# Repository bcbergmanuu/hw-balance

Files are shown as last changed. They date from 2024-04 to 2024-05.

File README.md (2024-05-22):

# Hardware deisgn balanceboard

Design Goals
  - Four measureable legs
  - USB 3 powered (<950mA)
  - Ultralow RMS Noise ldo (0.8µVRMS)
  - 10v Excitation voltage
  - Precision crystal clock fir filtering (20ppm)
  - Class c3 Loadcells type [LA250-D-100kg](https://allscaleseurope.com/content/uploads/2018/01/LA250-D-single-point-load-cell.pdf)
  - 8 bit decoupled auxiliary pc input
  - 24 bit ADC (ad7124)  

Balanceboard design

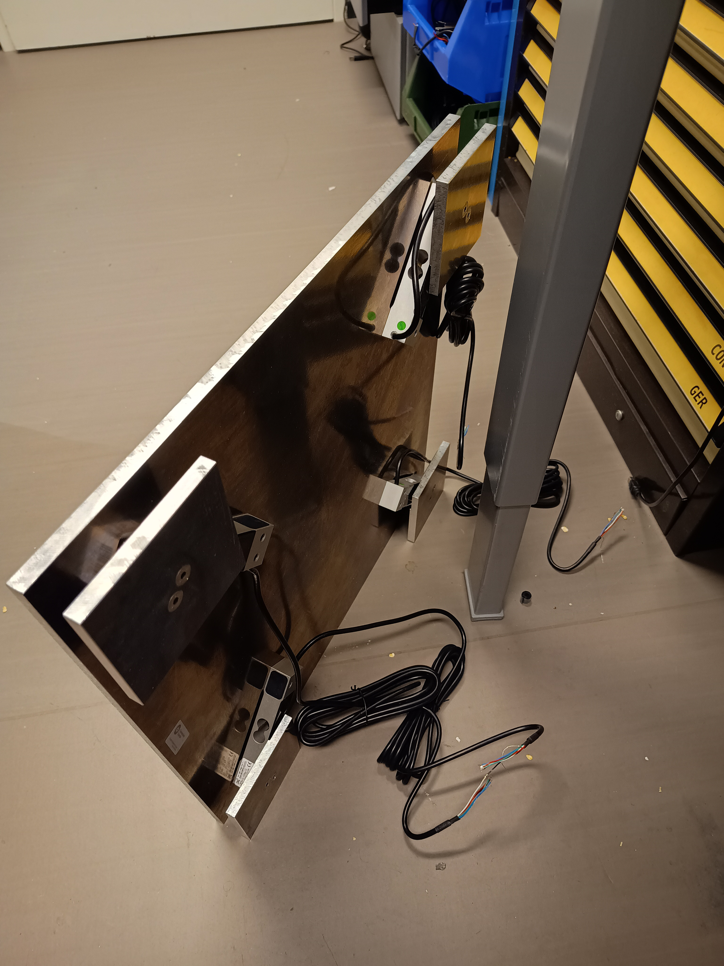
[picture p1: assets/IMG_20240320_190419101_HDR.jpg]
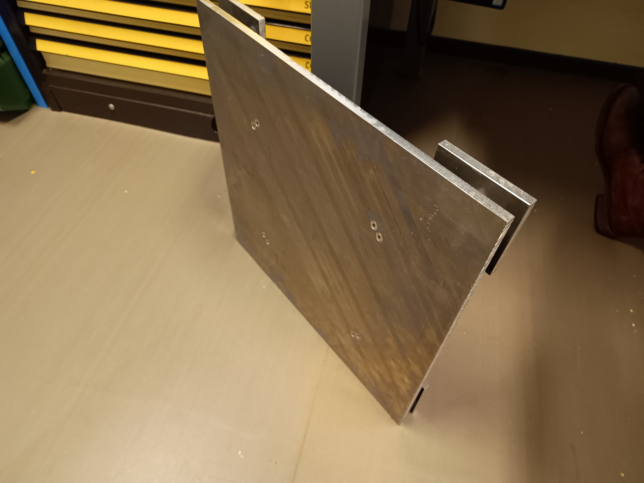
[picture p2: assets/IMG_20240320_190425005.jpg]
 

LTspice simulation LDO | Boost converters

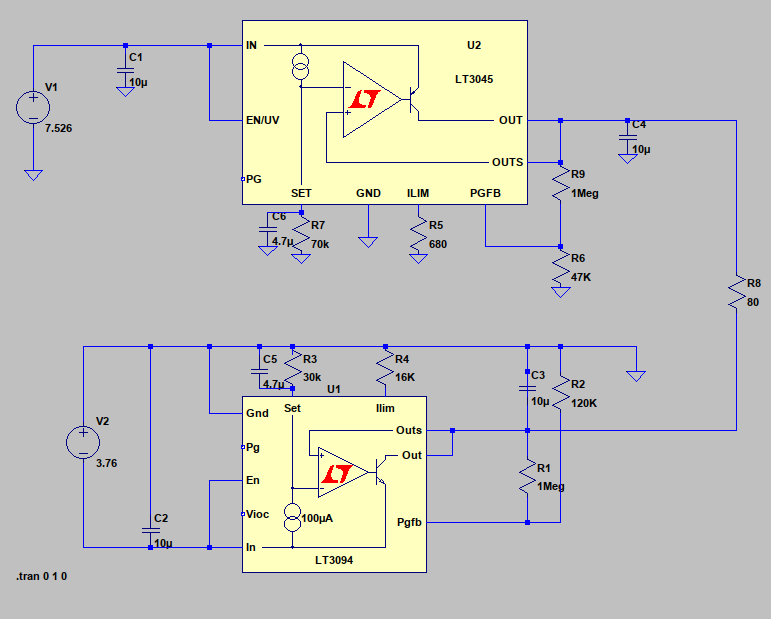
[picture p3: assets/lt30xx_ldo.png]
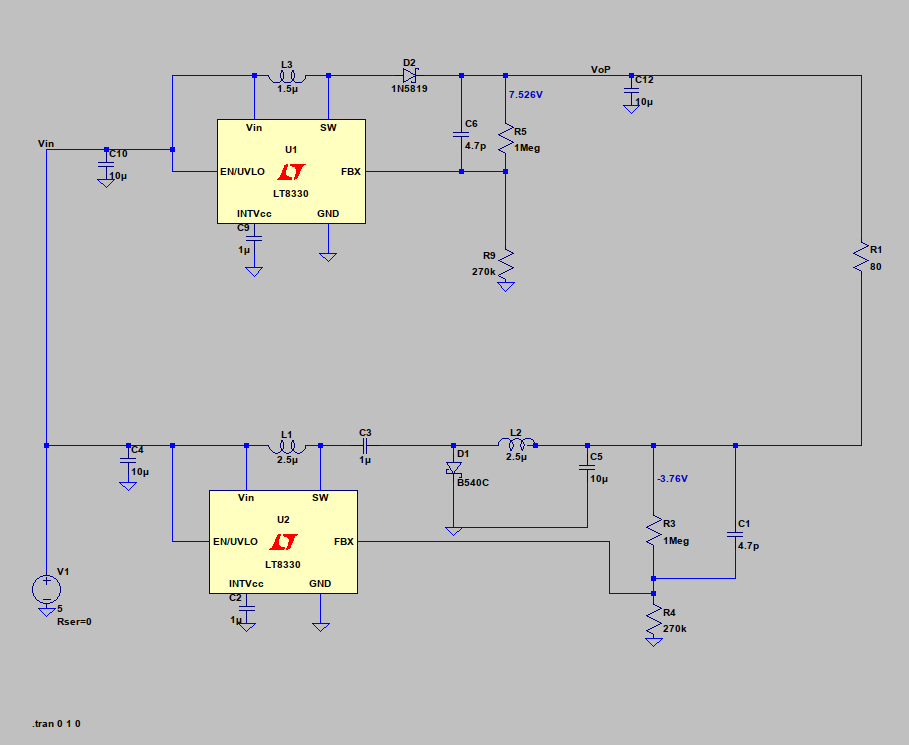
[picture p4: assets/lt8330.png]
 

Schematic Kicad | 3d-view of bcp

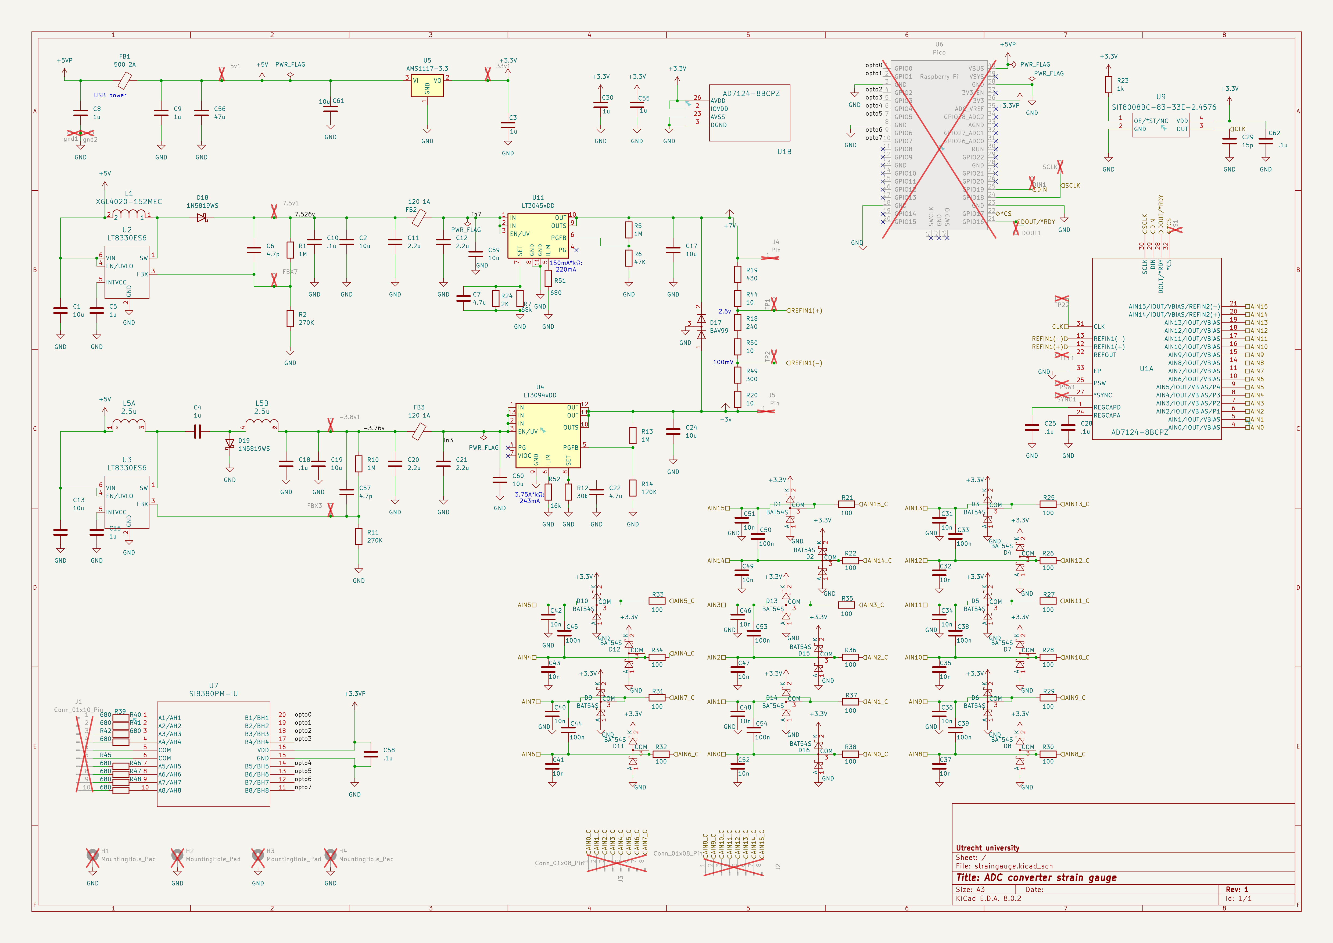
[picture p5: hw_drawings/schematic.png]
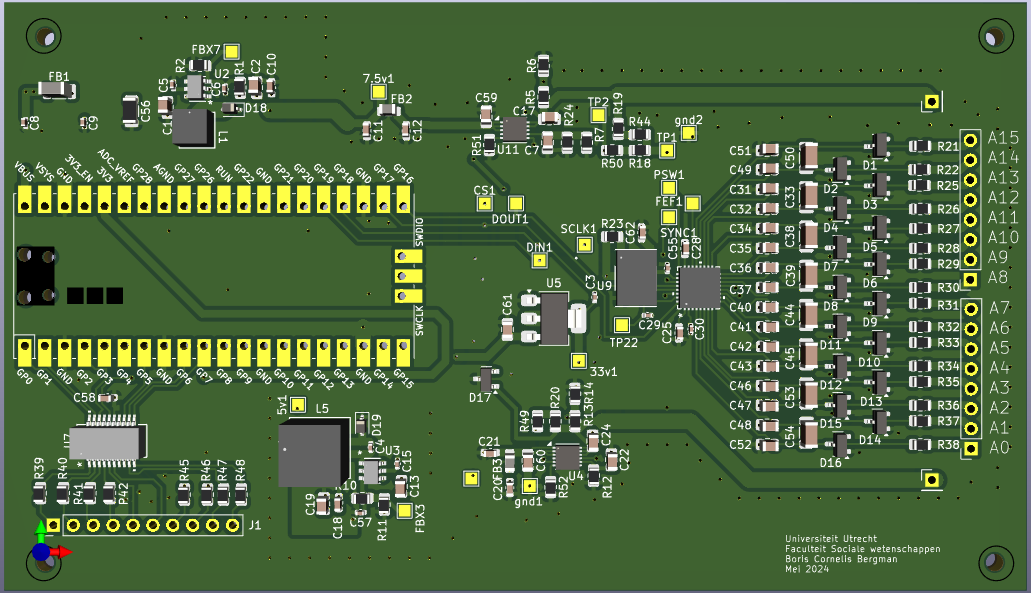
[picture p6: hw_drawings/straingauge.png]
 

Errata:
R19 48K, should be 390
R3 should be removed

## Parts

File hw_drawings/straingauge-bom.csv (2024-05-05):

Id | Designator | Footprint | Quantity | Designation | Supplier and ref
1 | U9 | SIT8008BC-83-33E-10.000000_SIT | 1 | SIT8008BC-83-33E-2.4576
2 | U5,U2 | 05-08-1699_ADI | 2 | LT8333RDD-PBF
3 | U1 | CP_32_12_ADI | 1 | AD7124-8BCPZ
4 | C23,C9,C5,C55,C8,C30,C15 | C_0402_1005Metric | 7 | 1u
5 | FBX7,FBX3,gnd2,7.5v1,PSW1,gnd1,TP2,TP22,DIN1,DOUT1,FEF1,-3.8v1,TP1,5v1,33v1,SYNC1,CS1,SCLK1 | TestPoint_Pad_1.5x1.5mm | 18 | ~
6 | C53,C33,C50,C39,C54,C38,C44,C45 | C_1206_3216Metric | 8 | 100n
7 | R24 | R_0805_2012Metric | 1 | 2K
8 | R6 | R_0805_2012Metric | 1 | 47K
9 | C20,C11,C12,C21 | C_0603_1608Metric | 4 | 2.2u
10 | R19 | R_0805_2012Metric | 1 | 430
11 | C56 | R_1206_3216Metric | 1 | 47u
12 | C43,C51,C34,C37,C31,C52,C40,C36,C49,C35,C48,C41,C47,C42,C32,C46 | C_0805_2012Metric | 16 | 10n
13 | J1 | PinHeader_1x10_P2.54mm_Vertical | 1 | Conn_01x10_Pin
14 | C57,C6 | C_0402_1005Metric | 2 | 4.7p
15 | CR2,CR3 | DIODE_DFN1608D-2_NEX | 2 | PMEG4020EPK_315
16 | R44,R50,R20 | R_0805_2012Metric | 3 | 10
17 | R3,R7 | R_0805_2012Metric | 2 | 68k
18 | R34,R28,R38,R25,R31,R32,R33,R36,R22,R27,R29,R37,R30,R21,R35,R26 | R_0805_2012Metric | 16 | 100
19 | D8,D16,D7,D2,D14,D9,D1,D4,D15,D3,D10,D6,D13,D11,D12,D5 | SOT-23 | 16 | BAT54S
20 | U4 | DFN-12-1EP_3x3mm_P0.45mm_EP1.65x2.38mm_ThermalVias | 1 | LT3094xDD
21 | R14 | R_0805_2012Metric | 1 | 120K
22 | R41,R45,R42,R48,R47,R39,R40,R46 | R_0805_2012Metric | 8 | 680
23 | R5,R16,R1,R10,R13 | R_0805_2012Metric | 5 | 1M
24 | C4,C25,C62,C14,C58,C10,C18,C28 | C_0603_1608Metric | 8 | .1u
25 | R43 | R_0805_2012Metric | 1 | 10k
26 | C13,C60,C24,C59,C1,C2,C19,C27,C17,C61 | C_0805_2012Metric | 10 | 10u
27 | L5 | IC4_MSD7342-252MLB_COC | 1 | 2.5u
28 | U7 | QSOP20_SIL | 1 | SI8380PM-IU
29 | R2,R11 | R_0805_2012Metric | 2 | 270K
30 | R4,R8 | R_0805_2012Metric | 2 | 20k
31 | C26,C22,C7 | C_0805_2012Metric | 3 | 4.7u
32 | J2,J3 | PinSocket_1x08_P2.54mm_Vertical | 2 | Conn_01x08_Pin
33 | L1 | IND_XGL4020_COC | 1 | XGL4020-152MEC
34 | L3,L4 | IND_NFZ18SM121SN10D_MUR | 2 | NFZ18SM121SN10D
35 | R23 | R_0805_2012Metric | 1 | 1k
36 | U6 | RPi_Pico_SMD_TH | 1 | Pico
37 | R15 | R_0805_2012Metric | 1 | 33k
38 | J4,J5 | PinHeader_1x01_P2.54mm_Vertical | 2 | Pin
39 | R18 | R_0805_2012Metric | 1 | 240
40 | R49 | R_0805_2012Metric | 1 | 300
41 | R17 | R_0805_2012Metric | 1 | 100k
42 | R9 | R_0805_2012Metric | 1 | 39k
43 | C29 | C_0402_1005Metric | 1 | 15p
44 | C3 | C_0603_1608Metric | 1 | 680p
45 | L2 | IND_742792040_WRE | 1 | 742792040
46 | U11,U10 | DFN-10-1EP_3x3mm_P0.5mm_EP1.65x2.38mm | 2 | LT3045xDD
47 | R12 | R_0805_2012Metric | 1 | 30k
48 | C16 | C_0603_1608Metric | 1 | 1.5n

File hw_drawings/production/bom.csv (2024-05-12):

Designator | Footprint | Quantity | Value | LCSC Part #
C1, C13, C17, C19, C2, C24, C59, C60, C61 | 0805 | 9 | 10u | C15850
C10, C18, C25, C28, C58, C62 | 0603 | 6 | .1u | C14663
C11, C12, C20, C21 | 0603 | 4 | 2.2u | C377773
C15, C3, C30, C4, C5, C55, C8, C9 | 0402 | 8 | 1u | C52923
C22, C7 | 0805 | 2 | 4.7u | C1779
C29 | 0402 | 1 | 15p | C1548
C31, C32, C34, C35, C36, C37, C40, C41, C42, C43, C46, C47, C48, C49, C51, C52 | 0805 | 16 | 10n | C441760
C33, C38, C39, C44, C45, C50, C53, C54 | 1206 | 8 | 100n | C338082
C56 | 1206 | 1 | 47u | C96123
C57, C6 | 0402 | 2 | 4.7p | C1569
D1, D10, D11, D12, D13, D14, D15, D16, D2, D3, D4, D5, D6, D7, D8, D9 | SOT-23 | 16 | BAT54S | C727126
D17 | SOT-23 | 1 | BAV99 | C2500
D18, D19 | D_SOD-323 | 2 | 1N5819WS | C191023
FB1 | 1206 | 1 | 500 2A | C515371
FB2, FB3 | 0805 | 2 | 120 1A | C2844587
L1 | IND_XGL4020_COC | 1 | XGL4020-152MEC
L5 | IC4_MSD7342-252MLB_COC | 1 | 2.5u
R1, R10, R13, R5 | 0805 | 4 | 1M | C17514
R11, R2 | 0805 | 2 | 270K | C17589
R12 | 0805 | 1 | 30k | C17621
R14 | 0805 | 1 | 120K | C17436
R18 | 0805 | 1 | 240 | C17572
R19 | 0805 | 1 | 430 | C17695
R20, R44, R50 | 0805 | 3 | 10 | C17415
R21, R22, R25, R26, R27, R28, R29, R30, R31, R32, R33, R34, R35, R36, R37, R38 | 0805 | 16 | 100 | C17408
R23 | 0805 | 1 | 1k | C17513
R24 | 0805 | 1 | 2K | C17604
R39, R40, R41, R42, R45, R46, R47, R48 | 0805 | 8 | 680 | C17798
R49 | 0805 | 1 | 300 | C17630
R51 | 0805 | 1 | 680
R52 | 0805 | 1 | 16k | C17490
R6 | 0805 | 1 | 47K | C17713
R7 | 0805 | 1 | 68k | C17801
U1 | CP_32_12_ADI | 1 | AD7124-8BCPZ | C97314
U11 | DFN-10-1EP_3x3mm_P0.5mm_EP1.65x2.38mm | 1 | LT3045xDD | C666574
U2, U3 | TSOT-23_S6_LIT | 2 | LT8330ES6 | C673741
U4 | DFN-12-1EP_3x3mm_P0.45mm_EP1.65x2.38mm_ThermalVias | 1 | LT3094xDD | C670492
U5 | SOT-223-3_TabPin2 | 1 | AMS1117-3.3 | C6186
U7 | QSOP20_SIL | 1 | SI8380PM-IU | C7315580
U9 | SIT8008BC-83-33E-10.000000_SIT | 1 | SIT8008BC-83-33E-2.4576

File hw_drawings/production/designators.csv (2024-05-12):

-3.8v1:1
33v1:1
5v1:1
7.5v1:1
C1:1
C10:1
C11:1
C12:1
C13:1
C15:1
C17:1
C18:1
C19:1
C2:1
C20:1
C21:1
C22:1
C24:1
C25:1
C28:1
C29:1
C3:1
C30:1
C31:1
C32:1
C33:1
C34:1
C35:1
C36:1
C37:1
C38:1
C39:1
C4:1
C40:1
C41:1
C42:1
C43:1
C44:1
C45:1
C46:1
C47:1
C48:1
C49:1
C5:1
C50:1
C51:1
C52:1
C53:1
C54:1
C55:1
C56:1
C57:1
C58:1
C59:1
C6:1
C60:1
C61:1
C62:1
C7:1
C8:1
C9:1
CS1:1
D1:1
D10:1
D11:1
D12:1
D13:1
D14:1
D15:1
D16:1
D17:1
D18:1
D19:1
D2:1
D3:1
D4:1
D5:1
D6:1
D7:1
D8:1
D9:1
DIN1:1
DOUT1:1
FB1:1
FB2:1
FB3:1
FBX3:1
FBX7:1
FEF1:1
H1:1
H2:1
H3:1
H4:1
J1:1
J2:1
J3:1
J4:1
J5:1
L1:1
L5:1
PSW1:1
R1:1
R10:1
R11:1
R12:1
R13:1
R14:1
R18:1
R19:1
R2:1
R20:1
R21:1
R22:1
R23:1
R24:1
R25:1
R26:1
R27:1
R28:1
R29:1
R30:1
R31:1
R32:1
R33:1
R34:1
R35:1
R36:1
R37:1
R38:1
R39:1
R40:1
R41:1
R42:1
R44:1
R45:1
R46:1
R47:1
R48:1
R49:1
R5:1
R50:1
R51:1
R52:1
R6:1
R7:1
SCLK1:1
SYNC1:1
TP1:1
TP2:1
TP22:1
U1:1
U11:1
U2:1
U3:1
U4:1
U5:1
U6:1
U7:1
U9:1
gnd1:1
gnd2:1

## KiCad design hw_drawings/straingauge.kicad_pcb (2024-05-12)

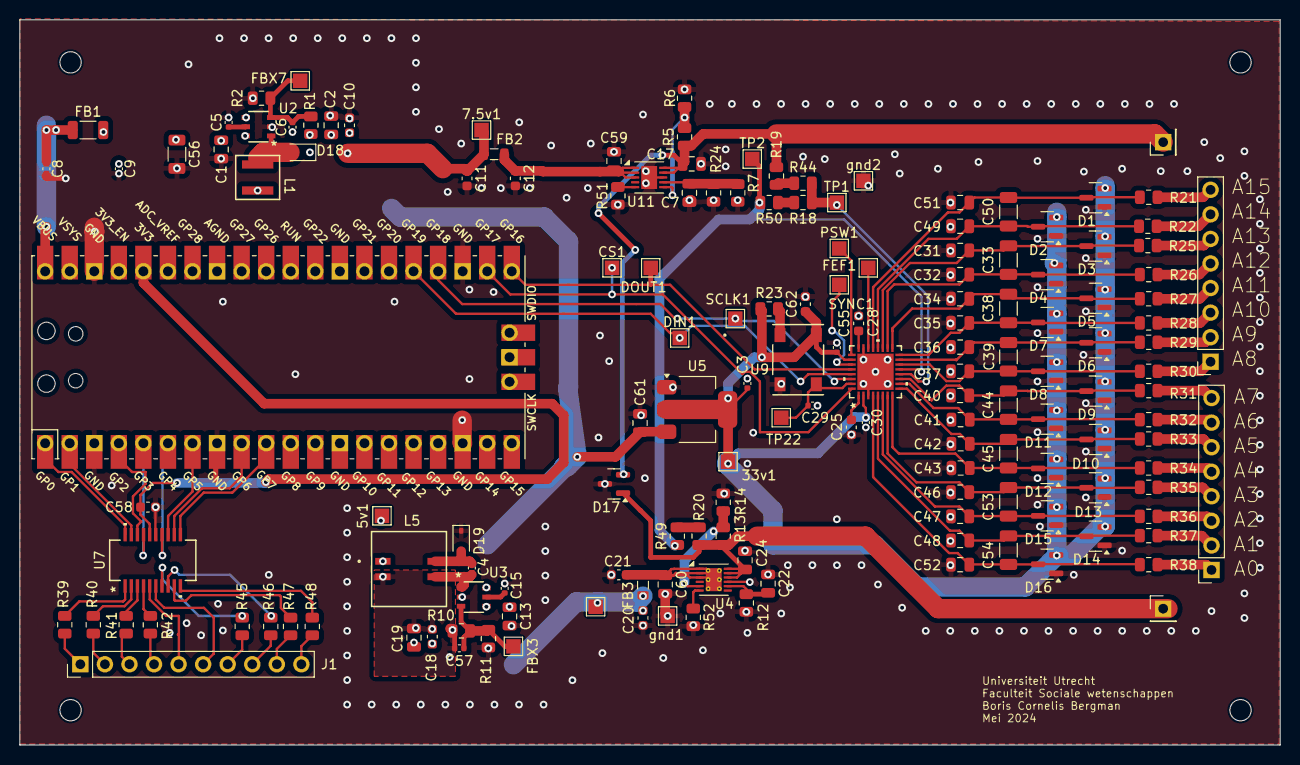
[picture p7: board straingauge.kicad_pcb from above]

Board: 4 copper layers, 130.3 x 75.0 mm, 161 parts (0 on the bottom side), 98 nets.

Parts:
5v1, 7.5v1, 33v1: TestPoint_Pad_1.5x1.5mm
-3.8v1: TestPoint_Pad_1.5x1.5mm
C1, C2, C13, C17, C19, C24, C59, C60, C61: 10u; C_0805_2012Metric
C3, C4, C5, C8, C9, C15, C30, C55: 1u; C_0402_1005Metric
C6, C57: 4.7p; C_0402_1005Metric
C7, C22: 4.7u; C_0805_2012Metric
C10, C18, C25, C28, C58, C62: .1u; C_0603_1608Metric
C11, C12, C20, C21: 2.2u; C_0603_1608Metric
C29: 15p; C_0402_1005Metric
C31, C32, C34, C35, C36, C37, C40, C41, C42, C43, C46, C47, C48, C49, C51, C52: 10n; C_0805_2012Metric
C33, C38, C39, C44, C45, C50, C53, C54: 100n; C_1206_3216Metric
C56: 47u; R_1206_3216Metric
CS1: TestPoint_Pad_1.5x1.5mm
D1, D2, D3, D4, D5, D6, D7, D8, D9, D10, D11, D12, D13, D14, D15, D16: BAT54S; SOT-23
D17: BAV99; SOT-23
D18, D19: 1N5819WS; D_SOD-323
DIN1: TestPoint_Pad_1.5x1.5mm
DOUT1: TestPoint_Pad_1.5x1.5mm
FB1: 500 2A; L_1206_3216Metric
FB2, FB3: 120 1A; L_0805_2012Metric
FBX3, FBX7: TestPoint_Pad_1.5x1.5mm
FEF1: TestPoint_Pad_1.5x1.5mm
H1, H2, H3, H4: MountingHole_Pad; MountingHole_2.2mm_M2
J1: Conn_01x10_Pin; PinHeader_1x10_P2.54mm_Vertical
J2, J3: Conn_01x08_Pin; PinSocket_1x08_P2.54mm_Vertical
J4, J5: Pin; PinHeader_1x01_P2.54mm_Vertical
L1: XGL4020-152MEC; IND_XGL4020_COC
L5: 2.5u; IC4_MSD7342-252MLB_COC
PSW1: TestPoint_Pad_1.5x1.5mm
R1, R5, R10, R13: 1M; R_0805_2012Metric
R2, R11: 270K; R_0805_2012Metric
R6: 47K; R_0805_2012Metric
R7: 68k; R_0805_2012Metric
R12: 30k; R_0805_2012Metric
R14: 120K; R_0805_2012Metric
R18: 240; R_0805_2012Metric
R19: 430; R_0805_2012Metric
R20, R44, R50: 10; R_0805_2012Metric
R21, R22, R25, R26, R27, R28, R29, R30, R31, R32, R33, R34, R35, R36, R37, R38: 100; R_0805_2012Metric
R23: 1k; R_0805_2012Metric
R24: 2K; R_0805_2012Metric
R39, R40, R41, R42, R45, R46, R47, R48, R51: 680; R_0805_2012Metric
R49: 300; R_0805_2012Metric
R52: 16k; R_0805_2012Metric
SCLK1: TestPoint_Pad_1.5x1.5mm
SYNC1: TestPoint_Pad_1.5x1.5mm
TP1, TP2, TP22: TestPoint_Pad_1.5x1.5mm
U1: AD7124-8BCPZ; CP_32_12_ADI
U2, U3: LT8330ES6; TSOT-23_S6_LIT
U4: LT3094xDD; DFN-12-1EP_3x3mm_P0.45mm_EP1.65x2.38mm_ThermalVias
U5: AMS1117-3.3; SOT-223-3_TabPin2
U6: Pico; RPi_Pico_SMD_TH
U7: SI8380PM-IU; QSOP20_SIL
U9: SIT8008BC-83-33E-2.4576; SIT8008BC-83-33E-10.000000_SIT
U11: LT3045xDD; DFN-10-1EP_3x3mm_P0.5mm_EP1.65x2.38mm
gnd1, gnd2: TestPoint_Pad_1.5x1.5mm

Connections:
+3.3V: 33v1.1, C3.1, C30.1, C55.1, C62.1, D1.2 (K), D2.2 (K), D3.2 (K), D4.2 (K), D5.2 (K), D6.2 (K), D7.2 (K), D8.2 (K), D9.2 (K), D10.2 (K), D11.2 (K), D12.2 (K), D13.2 (K), D14.2 (K), D15.2 (K), D16.2 (K), R23.1, U1.2 (IOVDD), U1.26 (AVDD), U5.2 (VO), U9.4 (VDD)
+3.3VP: C58.1, U6.36 (3V3), U7.16 (VDD)
+5V: 5v1.1, C1.1, C9.1, C13.1, C56.1, C61.1, FB1.2, L1.2, L5.1, U2.4 (EN/UVLO), U2.6 (VIN), U3.4 (EN/UVLO), U3.6 (VIN), U5.3 (VI)
+5VP: C8.1, FB1.1, U6.40 (VBUS)
+7V: C17.1, D17.2 (A), J4.1, R5.1, R19.1, U11.9 (OUTS), U11.10 (OUT)
-3v: C24.1, D17.1 (K), J5.1, R13.2, R20.2, U4.10 (OUTS), U4.11 (OUT), U4.12 (OUT)
/7.526v: 7.5v1.1, C2.1, C6.1, C10.1, C11.1, D18.1 (K), FB2.1, R1.1
/*CS: CS1.1, U1.32 (*CS), U6.22 (GPIO17)
/-3.76v: -3.8v1.1, C18.2, C19.1, C20.1, C57.1, FB3.1, L5.2, R10.2
/AIN0: C52.2, C54.1, D16.3 (COM), R38.1, U1.4 (AIN0/IOUT/VBIAS)
/AIN0_C: J3.1, R38.2
/AIN1: C48.1, C54.2, D14.3 (COM), R37.1, U1.5 (AIN1/IOUT/VBIAS)
/AIN1_C: J3.2, R37.2
/AIN2: C47.2, C53.1, D15.3 (COM), R36.1, U1.6 (AIN2/IOUT/VBIAS/P1)
/AIN2_C: J3.3, R36.2
/AIN3: C46.1, C53.2, D13.3 (COM), R35.1, U1.7 (AIN3/IOUT/VBIAS/P2)
/AIN3_C: J3.4, R35.2
/AIN4: C43.2, C45.1, D12.3 (COM), R34.1, U1.8 (AIN4/IOUT/VBIAS/P3)
/AIN4_C: J3.5, R34.2
/AIN5: C42.1, C45.2, D10.3 (COM), R33.1, U1.9 (AIN5/IOUT/VBIAS/P4)
/AIN5_C: J3.6, R33.2
/AIN6: C41.2, C44.1, D11.3 (COM), R32.1, U1.10 (AIN6/IOUT/VBIAS)
/AIN6_C: J3.7, R32.2
/AIN7: C40.1, C44.2, D9.3 (COM), R31.1, U1.11 (AIN7/IOUT/VBIAS)
/AIN7_C: J3.8, R31.2
/AIN8: C37.2, C39.1, D8.3 (COM), R30.1, U1.14 (AIN8/IOUT/VBIAS)
/AIN8_C: J2.1, R30.2
/AIN9: C36.1, C39.2, D6.3 (COM), R29.1, U1.15 (AIN9/IOUT/VBIAS)
/AIN9_C: J2.2, R29.2
/AIN10: C35.2, C38.1, D7.3 (COM), R28.1, U1.16 (AIN10/IOUT/VBIAS)
/AIN10_C: J2.3, R28.2
/AIN11: C34.1, C38.2, D5.3 (COM), R27.1, U1.17 (AIN11/IOUT/VBIAS)
/AIN11_C: J2.4, R27.2
/AIN12: C32.2, C33.1, D4.3 (COM), R26.1, U1.18 (AIN12/IOUT/VBIAS)
/AIN12_C: J2.5, R26.2
/AIN13: C31.1, C33.2, D3.3 (COM), R25.1, U1.19 (AIN13/IOUT/VBIAS)
/AIN13_C: J2.6, R25.2
/AIN14: C49.2, C50.1, D2.3 (COM), R22.1, U1.20 (AIN14/IOUT/VBIAS/REFIN2(+))
/AIN14_C: J2.7, R22.2
/AIN15: C50.2, C51.1, D1.3 (COM), R21.1, U1.21 (AIN15/IOUT/VBIAS/REFIN2(-))
/AIN15_C: J2.8, R21.2
/CLK: C29.1, TP22.1, U1.31 (CLK), U9.3 (OUT)
/DIN: DIN1.1, U1.29 (DIN), U6.25 (GPIO19)
/DOUT/*RDY: DOUT1.1, U1.28 (DOUT/*RDY), U6.21 (GPIO16)
/REFIN1(+): R18.1, R44.2, TP1.1, U1.12 (REFIN1(+))
/REFIN1(-): R49.1, R50.2, TP2.1, U1.13 (REFIN1(-))
/SCLK: SCLK1.1, U1.30 (SCLK), U6.24 (GPIO18)
/in3: C21.1, C60.1, FB3.2, U4.1 (IN), U4.2 (IN), U4.3 (EN/UV), U4.13 (IN)
/in7: C12.1, C59.1, FB2.2, U11.1 (IN), U11.2 (IN), U11.3 (EN/UV)
/opto0: U6.1 (GPIO0), U7.20 (B1/BH1)
/opto1: U6.2 (GPIO1), U7.19 (B2/BH2)
/opto2: U6.4 (GPIO2), U7.18 (B3/BH3)
/opto3: U6.5 (GPIO3), U7.17 (B4/BH4)
/opto4: U6.6 (GPIO4), U7.14 (B5/BH5)
/opto5: U6.7 (GPIO5), U7.13 (B6/BH6)
/opto6: U6.9 (GPIO6), U7.12 (B7/BH7)
/opto7: U6.10 (GPIO7), U7.11 (B8/BH8)
GND: C1.2, C2.2, C3.2, C5.1, C7.2, C8.2, C9.2, C10.2, C11.2, C12.2, C13.2, C15.1, C17.2, C18.1, C19.2, C20.2, C21.2, C22.1, C24.2, C25.2, C28.2, C29.2, C30.2, C31.2, C32.1, C34.2, C35.1, C36.2, C37.1, C40.2, C41.1, C42.2, C43.1, C46.2, C47.1, C48.2, C49.1, C51.2, C52.1, C55.2, C56.2, C58.2, C59.2, C60.2, C61.2, C62.2, D1.1 (A), D2.1 (A), D3.1 (A), D4.1 (A), D5.1 (A), D6.1 (A), D7.1 (A), D8.1 (A), D9.1 (A), D10.1 (A), D11.1 (A), D12.1 (A), D13.1 (A), D14.1 (A), D15.1 (A), D16.1 (A), D17.3 (K), D19.1 (K), R2.2, R6.2, R7.2, R11.1, R12.1, R14.1, R24.2, R51.2, R52.2, U1.3 (DGND), U1.23 (AVSS), U1.33 (EP), U2.2 (GND), U3.2 (GND), U4.9 (GND), U5.1 (GND), U6.3 (GND), U6.8 (GND), U6.18 (GND), U6.23 (GND), U6.38 (GND), U7.15 (GND), U9.2 (GND), U11.8 (GND), U11.11 (GND), gnd1.1, gnd2.1
unnamed: D18.2 (A), L1.1, U2.1 (SW)
unnamed: C4.2, D19.2 (A), L5.4
unnamed: J1.1, R39.1
unnamed: J1.2, R40.1
unnamed: J1.3, R41.1
unnamed: J1.4, R42.1
unnamed: J1.5, U7.5 (COM)
unnamed: J1.6, U7.6 (COM)
unnamed: J1.7, R45.1
unnamed: J1.8, R46.1
unnamed: J1.9, R47.1
unnamed: J1.10, R48.1
unnamed: R18.2, R50.1
unnamed: R19.2, R44.1
unnamed: R20.1, R49.2
unnamed: SYNC1.1, U1.27 (*SYNC)
unnamed: PSW1.1, U1.25 (PSW)
unnamed: FEF1.1, U1.22 (REFOUT)
unnamed: C28.1, U1.24 (REGCAPA)
unnamed: C25.1, U1.1 (REGCAPD)
unnamed: C6.2, FBX7.1, R1.2, R2.1, U2.3 (FBX)
unnamed: C5.2, U2.5 (INTVCC)
unnamed: C57.2, FBX3.1, R10.1, R11.2, U3.3 (FBX)
unnamed: C15.2, U3.5 (INTVCC)
unnamed: C4.1, L5.3, U3.1 (SW)
unnamed: R52.1, U4.6 (ILIM)
unnamed: R13.1, R14.2, U4.5 (PGFB)
unnamed: C22.2, R12.2, U4.8 (SET)
unnamed: R39.2, U7.1 (A1/AH1)
unnamed: R40.2, U7.2 (A2/AH2)
unnamed: R41.2, U7.3 (A3/AH3)
unnamed: R42.2, U7.4 (A4/AH4)
unnamed: R45.2, U7.7 (A5/AH5)
unnamed: R46.2, U7.8 (A6/AH6)
unnamed: R47.2, U7.9 (A7/AH7)
unnamed: R48.2, U7.10 (A8/AH8)
unnamed: R23.2, U9.1 (OE/*ST/NC)
unnamed: R51.1, U11.5 (ILIM)
unnamed: R5.2, R6.1, U11.6 (PGFB)
unnamed: C7.1, R7.1, R24.1, U11.7 (SET)

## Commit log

2024-04-29 drawing schematic
    [straingauge.kicad_pcb, straingauge.kicad_sch]
2024-04-30 finished schematic
    [straingauge.kicad_pcb, straingauge.kicad_sch]
2024-05-02 fixed ERC
    [straingauge.kicad_pcb, straingauge.kicad_sch]
2024-05-03 full pcb
    [straingauge.kicad_pcb, straingauge.kicad_sch]
2024-05-03 full pcb1
    [straingauge.kicad_pcb, straingauge.kicad_sch]
2024-05-05 finished project
    [straingauge-bom.csv, straingauge-job.gbrjob, straingauge.csv, straingauge.kicad_pcb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]
2024-05-05 changed bead
    [bom.csv, designators.csv, positions.csv, straingauge.kicad_pcb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]
2024-05-06 move l5
    [bom.csv, positions.csv, straingauge.kicad_pcb, straingauge.kicad_sch]
